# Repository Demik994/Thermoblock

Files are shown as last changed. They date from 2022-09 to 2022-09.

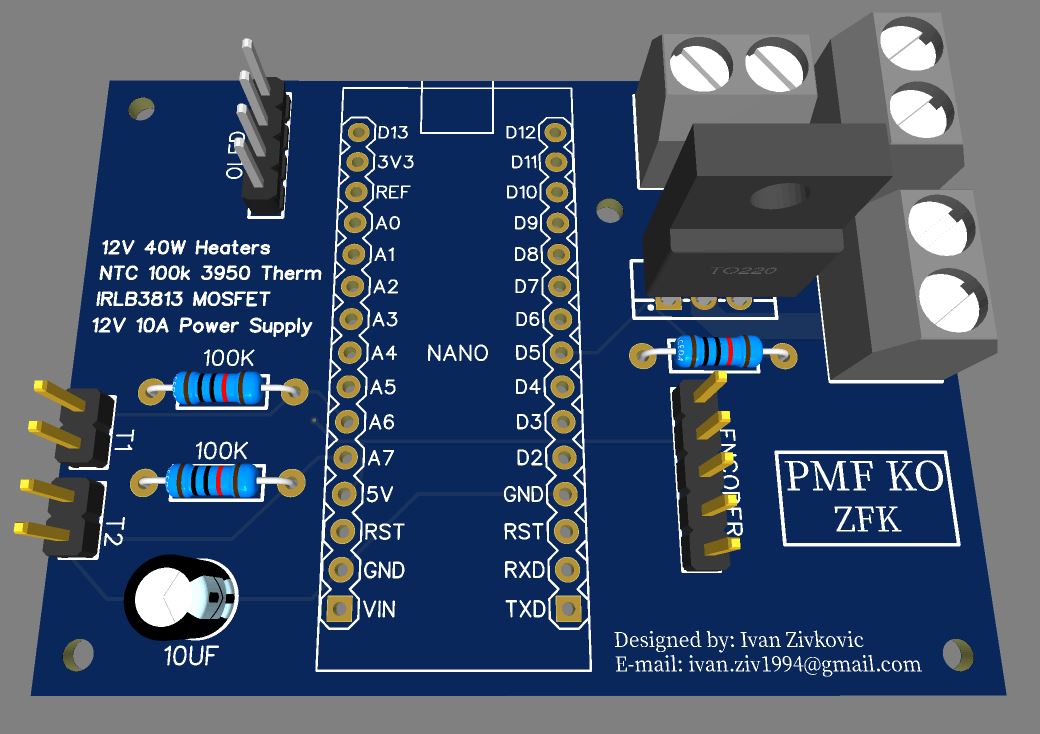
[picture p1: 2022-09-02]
EasyEDA/PCB_3D_Thermoblock.JPG

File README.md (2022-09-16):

# **Thermoblock**

###### By Ivan Zivkovic

## About the Project

As a chemistry student, I have always strived to learn new skills applicable to scientific experiments. 
This project not only helped me learn how to prepare and eventually make electronic schematics as well as PCB layouts but also improve my programming and 3D modelling skills. 
I would very much so appreciate if you could point out the mistakes I have made because I believe there is no better way to get move forward than to analyze past mistakes, draw conclusions and eventually progress. 
The initial idea behind this project was to monitor how temperature affects the thickness of the polyelectrolyte multilayer (PEM) by heating up the aluminum block placed on an ellipsometer pedestal with a sample on it.
Of course, this is a general-purpose heater. In the future, I would like to upgrade the process by making a 3D filament dehydrator.

Goal was also to develop Thermoblock with readily available components but at the same time keep PCB partially modular. That way, a user can take advantage of utilizing different I2C displays (certain code modifications are required) or different heaters.
This PCB uses following components:

  - 0.91" OLED Display
  - 2x 40W 12V Heaters (the ones most 3D printer hotends use)
  - 2x 100k Ohm NTC Thermistors
  - KY-040 Rotary Encoder Module
  - Arduino Nano (I know this could all be done with the 328P but I don't have SMD soldering station nor knowledge to do that, YET)
  - MOSFET IRL83813
  - 2x 100k Ohm Resistors
  - 10k Ohm resistor
  - 10 uF Capacitor
  - 3 Clamp Terminals
  - 2x 2-pin Male Strip
  - 4-pin Male Strip
  - 5-pin Male Strip
  - 12V 8A Power Supply (I used 350W old PC PSU)

The software uses following libraries:

  - https://github.com/Dlloydev/QuickPID
  - https://github.com/Stutchbury/EncoderButton
  - https://github.com/adafruit/Adafruit_SSD1306
  - https://github.com/adafruit/Adafruit-GFX-Library

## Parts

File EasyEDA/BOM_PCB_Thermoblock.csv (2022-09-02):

ID | Name | Designator | Footprint | Quantity | Manufacturer Part | Manufacturer | Supplier | Supplier Part | Price
1 | 10uF | 10UF | CAP-D5.0×F2.0 | 1
2 | 31001102 | 12V,HEATER1,HEATER2 | CONN-TH_2P-P5.08_31001102 | 3 | 31001102 | METZ CONNECT | LCSC | C123210 | 0.227
3 | Header-Male-2.54_1x4_C59481 | OLED | HDR-TH_4P-P2.54-V-M | 1 | Headers Pins 1*4P | ReliaPro | LCSC | C59481 | 0.012
4 | Header-Male-2.54_1x2 | T1,T2 | HDR-TH_2P-P2.54-V-M-1 | 2 | 826629-2 | TE Connectivity | LCSC | C86471 | 0.34
5 | HDR-M-2.54_1x5 | ENCODER | HDR-M-2.54_1X5 | 1 |  |  | LCSC | C358687 | 0.03
6 | IRLB3813PBF | MOSFET | ITO-220AB-3_L10.2-W4.5-P2.60-L | 1 | IRLB3813PBF | Infineon | LCSC | C148140 | 1.874
7 | 100k | 100K | R_AXIAL-0.4 | 2
8 | 10k | 10K | R_AXIAL-0.4 | 1
9 | ARDUINO_NANO | NANO | COMM-TH_ARDUINO_NANO | 1 | ARDUINO_NANO | null | LCSC | C9900017879

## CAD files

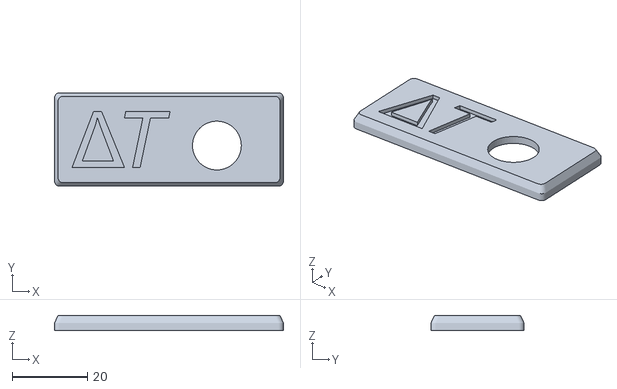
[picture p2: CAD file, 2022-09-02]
Housing/EncoderCover.stl
61.0 x 24.8 x 4.00

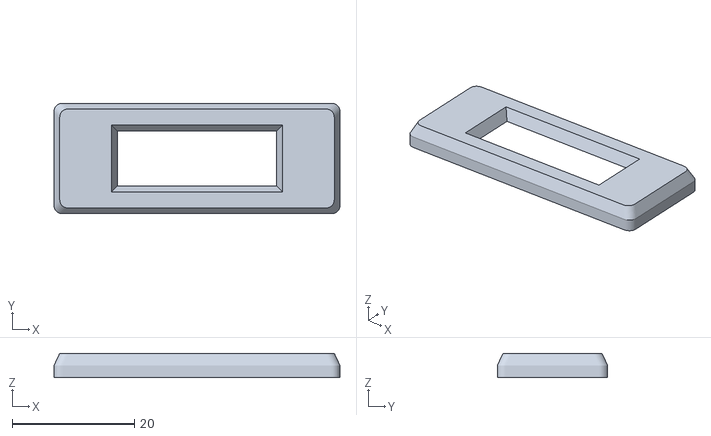
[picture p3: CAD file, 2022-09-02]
Housing/DisplayCover.stl
46.7 x 18.0 x 4.00

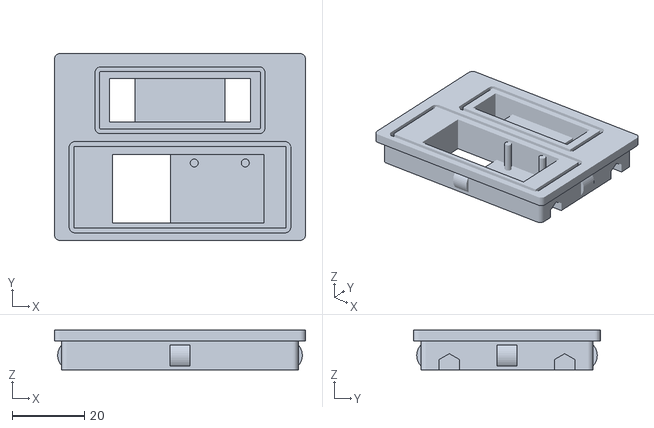
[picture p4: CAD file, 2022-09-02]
Housing/Cover.stl
69.6 x 51.8 x 11.0

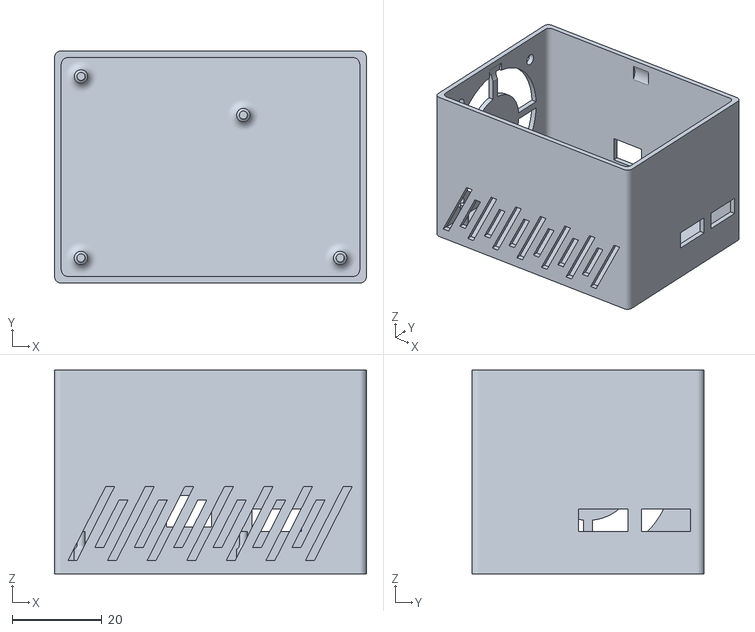
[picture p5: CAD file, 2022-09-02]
Housing/Housing.stl
69.6 x 51.8 x 45.5

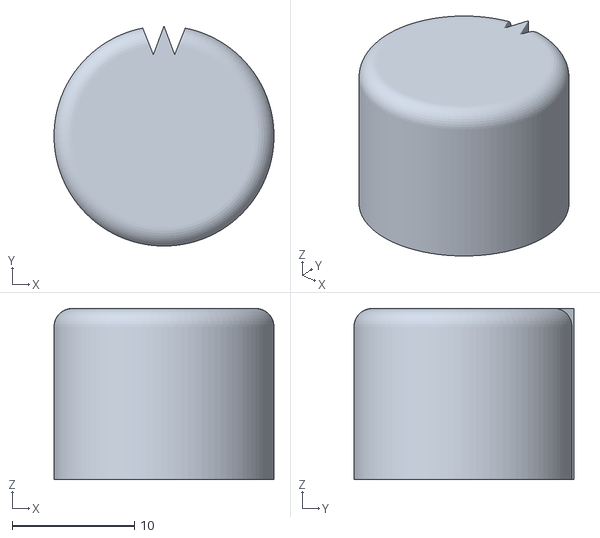
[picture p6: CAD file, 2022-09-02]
Housing/EncoderCap.stl
18.0 x 18.0 x 14.0

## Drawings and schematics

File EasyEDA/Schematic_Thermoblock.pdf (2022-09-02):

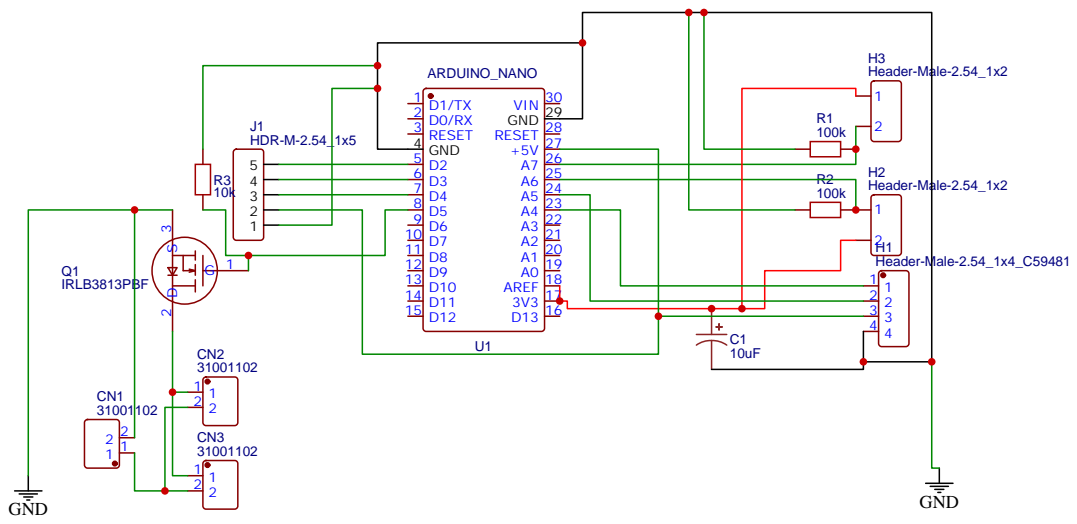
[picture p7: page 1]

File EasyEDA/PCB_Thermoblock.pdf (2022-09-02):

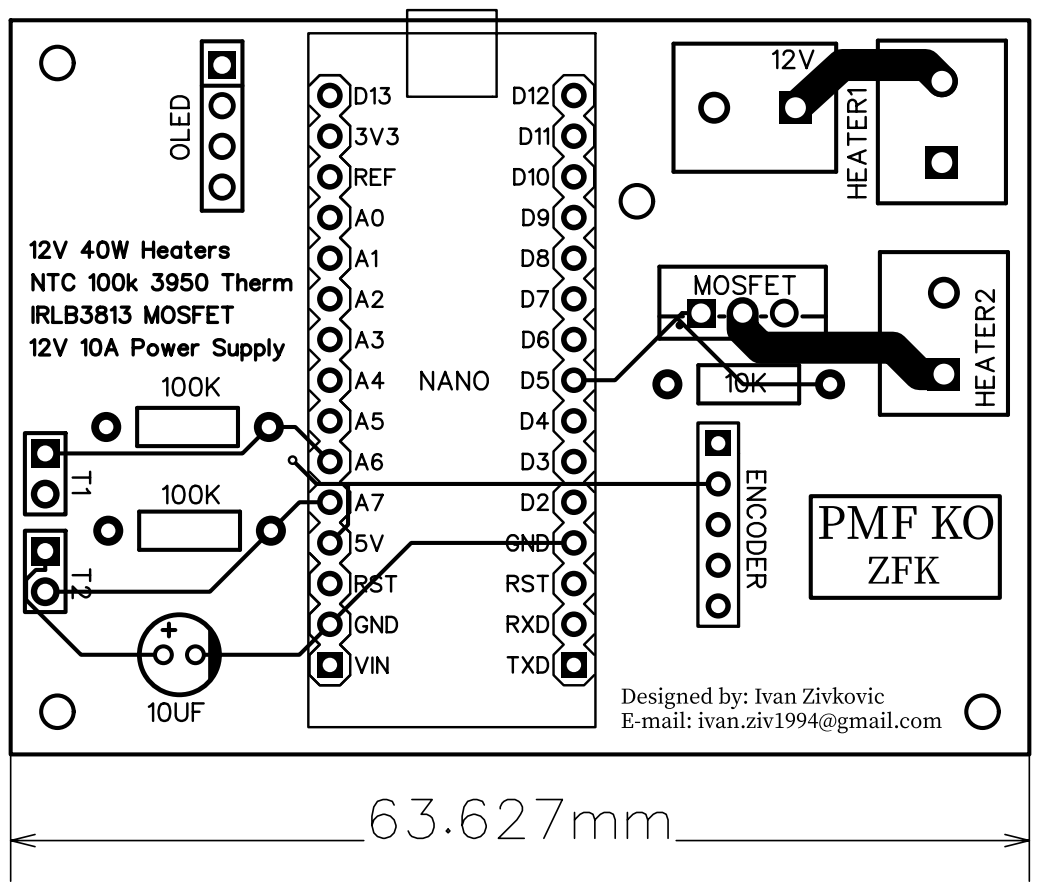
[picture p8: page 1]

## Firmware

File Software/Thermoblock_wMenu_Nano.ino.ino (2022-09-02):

#include <QuickPID.h>
#include <SPI.h>
#include <Wire.h>
#include <EncoderButton.h>
#include <Wire.h>
#include <Adafruit_SSD1306.h>
#include <Adafruit_GFX.h>
#include <math.h>

// pins
#define thermPin1 A6
#define thermPin2 A7
#define encoderPin1 2
#define encoderPin2 3
#define switchPin 4
#define heaterPin 5
#define OLED_RESET     -1

#define SCREEN_WIDTH 128 // OLED display width, in pixels
#define SCREEN_HEIGHT 32 // OLED display height, in pixels


#define SCREEN_ADDRESS 0x3C ///< See datasheet for Address; 0x3D for 128x64, 0x3C for 128x32
Adafruit_SSD1306 display(SCREEN_WIDTH, SCREEN_HEIGHT, &Wire, OLED_RESET);

// constants
int avgSize = 10; // averaging size

float R1 = 100000; // NTC and voltage divider resistance in Ohms
float c1 = 1.009249522e-03, c2 = 2.378405444e-04, c3 = 2.019202697e-07; //NTC thermistor coefficients

const unsigned long windowSize = 2000; //PID time period
const byte debounce = 50; //PID debounce
float Input, Output, Setpoint = 0, Kp = 20, Ki = 10, Kd = 45.0; //PID coefficients

float avgT; //average temperature from both thermistors
float avgT1; //average temperature from thermistor #1
float avgT2; //average temperature from thermistor #2

int initialT; //initial temperature
int setpointT; //temperature set by user

byte clickState; //detecting encoder click
bool doubleClickState = false; //detecting encoder double click
byte menuCount = 0; //menu manager
byte dir = 0; //encoder direction
bool runState = false; //is heater running or not

int Vo; //thermistor voltage
float logR2, R2; //thermistor resistance and logarithm

// status
unsigned long windowStartTime, nextSwitchTime;
boolean relayStatus = false;

QuickPID myPID(&Input, &Output, &Setpoint, Kp, Ki, Kd,
               myPID.pMode::pOnError,
               myPID.dMode::dOnMeas,
               myPID.iAwMode::iAwClamp,
               myPID.Action::direct);

/**
 * Instatiate an EncoderButton.
 * For Arduino Uno, the hardware interrupts are pins 2 & 3
 * Encoder+button:
 * EncoderButton(byte encoderPin1, byte encoderPin2, byte switchPin);
 * Encoder only:
 * EncoderButton(byte encoderPin1, byte encoderPin2);
 * Button only:
 * EncoderButton(byte switchPin);
 */
EncoderButton eb1(encoderPin1, encoderPin2, switchPin);
volatile unsigned int encoder0Pos = 0;

/**
 * A function to handle the 'clicked' event
 * Can be called anything but requires EncoderButton& 
 * as its only parameter.
 */
void onEb1Clicked(EncoderButton& eb) {
  
  if (eb.clickCount() == 1) {
    clickState = LOW;
    //eb.position() == 0;
    //encoder0Pos = 0;
  }
  if (eb.clickCount() == 2) {
    doubleClickState = true;
    
  }
  
}

/**
 * A function to handle the 'encoder' event
 */
void onEb1Encoder(EncoderButton& eb) {
  
  if (eb.increment() > 0) {
    encoder0Pos += 1;
  }
  if (eb.increment() < 0) {
    encoder0Pos -= 1;
  }

  
}

void setup() {
  // put your setup code here, to run once:
  Serial.begin(9600);
  delay(500);
  if(!display.begin(SSD1306_SWITCHCAPVCC, SCREEN_ADDRESS)) {
    Serial.println(F("SSD1306 allocation failed"));
    for(;;); // Don't proceed, loop forever
  }

  // Show initial display buffer contents on the screen --
  // the library initializes this with an Adafruit splash screen.
  display.display();
  delay(1000); // Pause for 1 second

  // Clear the buffer
  display.clearDisplay();
  
  pinMode(thermPin1, INPUT);
  pinMode(thermPin2, INPUT);
  pinMode(heaterPin, OUTPUT);
  

  analogReference(EXTERNAL); //AREF pin is connected to Arduino 3.3V output pin for a more stable signal

  
  myPID.SetOutputLimits(0, windowSize);
  myPID.SetSampleTimeUs(windowSize * 1000);
  myPID.SetMode(myPID.Control::automatic);

  //Link the event(s) to your function
  eb1.setClickHandler(onEb1Clicked);
  eb1.setEncoderHandler(onEb1Encoder);
  
}

void loop() {
  // You must call update() for every defined EncoderButton.
  // This will update the state of the encoder & button and 
  // fire the appropriate events.
  clickState = HIGH;
  eb1.update();
  menuCheck();
  staticMenu(tempRead(1), tempRead(2), tempRead(3), setpointT);
  Setpoint = setpointT;
  heaterControl();     
  display.clearDisplay();
}

float tempRead(int sensorValue) {
  float T_sum = 0.0; //sum of temperatures for averaging
  
  if (sensorValue == 1) {
    for (int i=0 ; i<avgSize ; i++){
      
      Vo = analogRead(thermPin1);
      R2 = R1/10 * (1023.0 / (float)Vo - 1.0);
      logR2 = log(R2);
      T_sum += ((1.0 / (c1 + c2*logR2 + c3*logR2*logR2*logR2))-273);
      
      
        
    }
    avgT = T_sum/float(avgSize);
  }

  if (sensorValue == 2) {
    for (int i=0 ; i<avgSize ; i++){
              
      Vo = analogRead(thermPin2);
      R2 = R1/10 * (1023.0 / (float)Vo - 1.0);
      logR2 = log(R2);
      T_sum += ((1.0 / (c1 + c2*logR2 + c3*logR2*logR2*logR2))-273);
      
        
    }
    avgT = T_sum/float(avgSize);
  }

  if (sensorValue == 3) {
    for (int i=0 ; i<avgSize ; i++){
      
      Vo = analogRead(thermPin1);
      R2 = R1/10 * (1023.0 / (float)Vo - 1.0);
      logR2 = log(R2);
      T_sum += ((1.0 / (c1 + c2*logR2 + c3*logR2*logR2*logR2))-273);
      
      Vo = analogRead(thermPin2);
      R2 = R1/10 * (1023.0 / (float)Vo - 1.0);
      logR2 = log(R2);
      T_sum += ((1.0 / (c1 + c2*logR2 + c3*logR2*logR2*logR2))-273);
      
        
    }
    avgT = T_sum/(2*float(avgSize));
  }
 
  return avgT; //returns average temperature for called sensor(s)
}

void staticMenu(float avgT1, float avgT2, float avgT, int setpoint) {
 
    
  //---------------------------------
  display.setTextSize(1);
  display.setTextColor(SSD1306_WHITE);
  display.setCursor(1, 0);
  display.print("T1:");
  display.println(round(avgT1));
 
  display.setCursor(46, 0);
  display.print("T2:");
  display.println(round(avgT2));
  
  display.setCursor(91, 0);
  display.print("Ta:");
  display.println(round(avgT));
  
  
  
  display.setTextSize(1);
  display.setCursor(10, 10);
  display.println("Setpoint:");
  display.setCursor(65, 10);
  display.println(setpoint);

  

  display.setCursor(10, 20);
  display.println("Start:");
  display.setCursor(45, 20);
  if (doubleClickState == true && menuCount == 1) { //if double clicked and cursor set on "Start:" changes heater state
    runState = !runState;   
  }

  if (doubleClickState == true && menuCount == 0) { //if double clicked and cursor set on "Setpoint:" resets setpoint temperature
    setpointT = 0;  
  }


  if (runState == true) {
    display.println("Run!");
  }  
          
  if (runState == false) {
    display.println("Idle");
  }
  doubleClickState = false; 

  display.setCursor(2, (menuCount * 10) + 10); //changing cursor position
  display.println(">");

  display.display();
}

void heaterControl() {
  if (runState == true) {
    unsigned long msNow = millis();
    Input = tempRead(3); // average temperature from both sensors
    if (Setpoint < avgT) {
      Setpoint -= 10; //temperature setpoint correction because of overshoot, could be different value, not from original QuickPID
      if (myPID.Compute()) windowStartTime = msNow;

    if (!relayStatus && Output > (msNow - windowStartTime)) {
      if (msNow > nextSwitchTime) {
        nextSwitchTime = msNow + debounce;
        relayStatus = true;
        digitalWrite(heaterPin, HIGH);
        
      }
    } else if (relayStatus && Output < (msNow - windowStartTime)) {
      if (msNow > nextSwitchTime) {
        nextSwitchTime = msNow + debounce;
        relayStatus = false;
        digitalWrite(heaterPin, LOW);
      }
    }
    Setpoint += 10;
    }
    if (Setpoint >= avgT) {
      Setpoint += 10; //temperature setpoint correction because of overshoot, could be different value
      if (myPID.Compute()) windowStartTime = msNow;

    if (!relayStatus && Output > (msNow - windowStartTime)) {
      if (msNow > nextSwitchTime) {
        nextSwitchTime = msNow + debounce;
        relayStatus = true;
        digitalWrite(heaterPin, HIGH);
        
      }
    } else if (relayStatus && Output < (msNow - windowStartTime)) {
      if (msNow > nextSwitchTime) {
        nextSwitchTime = msNow + debounce;
        relayStatus = false;
        digitalWrite(heaterPin, LOW);
      }
    }
    Setpoint -= 10; //temperature setpoint correction because of overshoot, could be different value
    }    
  }    
}
void menuCheck() {
  if (clickState == LOW && menuCount < 2) {
    menuCount++;
  }

  if (clickState == LOW && menuCount >= 2) { //resets cursor to first option
    menuCount = 0;
    encoder0Pos = 0;
  }

  if (menuCount == 0) {
    initialT = encoder0Pos;
    encoder0Pos = 0;
    setpointT += initialT;
    setpointT = constrain(setpointT, 0, 250);    
  }  
}
